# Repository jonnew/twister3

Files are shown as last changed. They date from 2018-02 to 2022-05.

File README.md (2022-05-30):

# Twister3
Twister3 is a simple and fast microwire twister from the [Wilson
Lab](http://web.mit.edu/wilsonlab/) at MIT. It is used to make tetrodes and
stereotrodes for invasive neural recordings. It can be purchased from the 
[Open Ephys store](https://open-ephys.org/twister-3).

Twister3

### Documentation
Construction, usage, and performance information is provided in the [Twister3
manuscript](https://www.biorxiv.org/content/10.1101/727644v1). Please cite 
this paper if you use Twister3 in your research. If you have further questions, 
please direct them toward the [Open Ephys forum](https://groups.google.com/forum/#!forum/open-ephys).

### Licensing
Copyright Jonathan P. Newman & Jakob Voigts 2020

<br />This work is licensed under a <a rel="license" href="http://creativecommons.org/licenses/by-nc-sa/3.0/igo/">Creative Commons Attribution-NonCommercial-ShareAlike 3.0 IGO License</a>.

If your are interested in obtaining a license to sell this device, please contact us at https://open-ephys.org/contact

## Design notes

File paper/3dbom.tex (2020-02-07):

%\externaldocument{twister3}
\setlength{\tabcolsep}{3pt}

\begin{table}[!htbp]
\centering
\caption{3D-printing bill of materials. An continuously updated bill of
    materials is located on
    \href{https://docs.google.com/spreadsheets/d/1tdc3wfE6V87q8yqBOQvDj7WylAztkh6_2kuL-YzyB0g/edit\#gid=0}{this
    Google sheet}. The right-most column provides links to order parts from each supplier.}
\label{t:3d_bom}

\begin{tabular}{llllll}
\multicolumn{4}{l}{\textit{\textbf{3D-Printing Bill of Materials}}} \\
\toprule
\textbf{Qty} &
\textbf{Description} &
\textbf{Material} &
\textbf{Supplier} &
\textbf{STL File in Repository} &
\textbf{Link} \\
\midrule

% AUTOGENERATED
1 & Feeder Base & Nylon PA12 & Shapeways & \verb|twister3_arm-base.STL| & \url{http:/shpws.me/QtfT} \\
1 & Motor Mount & Nylon PA12 & Shapeways & \verb|twister3_motor-mount.STL| & \url{http:/shpws.me/QtfL} \\
1 & Bobbin Shield & ``Fine detail plastic'' & Shapeways & \verb|twister3_bobbin-shield.STL| & \url{http:/shpws.me/QtfU}\\
2 & Bobbin Spacer & ``Fine detail plastic'' & Shapeways & \verb|twister3_bobbin-spacer.STL| & \url{http:/shpws.me/QtfR} \\
2 & Bobbin Washer & ``Fine detail plastic'' & Shapeways & \verb|twister3_bobbin-washer.STL| & \url{http:/shpws.me/QtfP} \\
4 & Bobbin & ``Fine detail plastic'' & Shapeways & \verb|twister3_bobin.STL| & \url{http:/shpws.me/QtfM} \\
1 & Rotor Base & ``Fine detail plastic'' & Shapeways & \verb|twister3_rotor-base.STL| & \url{http:/shpws.me/QtfK} \\
1 & Adjustment Plate  & ``Fine detail plastic'' & Shapeways & \verb|twister3_adjustment-plate.STL| & \url{http://shpws.me/Rekt} \\
1 & Wire Guide & ``Fine detail plastic'' & Shapeways & \verb|twister3_wire-guide-base.STL| & \url{http:/shpws.me/QtfI} \\
2 & Stock Spool Bearing Case & ``Fine detail plastic'' & Shapeways & \verb|twister3_stock-spool-bearing-case.STL| & \url{http:/shpws.me/QUtz} \\
1 & Twist Wire Aligner & Rhodium plated brass & Shapeways & \verb|twister3_twist-aligner.STL| & \url{http://shpws.me/R6mo} \\
1 & Spring Rotor Top & PEBA 2301 & Sculpteo & \verb|twister3_spring-top.STL| & \url{https://bit.ly/2H32cna} \\

\bottomrule
\end{tabular}
\end{table}

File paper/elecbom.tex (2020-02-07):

%\externaldocument{twister3}
\setlength{\tabcolsep}{3pt}

\begin{table}[!htbp]
\centering
\caption{Control box (Fig.~\ref{f:ctrl_box}) bill of materials. A continuously
    updated bill of materials is located on
    \href{https://docs.google.com/spreadsheets/d/1tdc3wfE6V87q8yqBOQvDj7WylAztkh6_2kuL-YzyB0g/edit\#gid=0}{this
    Google sheet}. Table entries labeled ``common'' are ubiquitous and
    therefore listing specific part numbers is futile due to rapid supplier
    turn over. PCB design files are located at this
    \href{https://github.com/jonnew/twister3/tree/master/control-board}{link}.
    The PCB is split into two halves separated by a breakaway v-cut. One half
    serves as the top panel of the enclosure, visible in (Fig.~\ref{f:ctrl_box}
    (B)), and the other has all electronics and is mounted beneath the front
panel.}
\label{t:elec_bom}

\begin{tabular}{lllllll}
\multicolumn{6}{l}{\textit{\textbf{Control Box Bill of Materials}}} \\
\toprule
\textbf{Qty} &
\textbf{Schematic Name} &
\textbf{Schematic Value} &
\textbf{Description} &
\textbf{Supplier} &
\textbf{Supplier Part No.} &
\textbf{Manufacturer Part No.} \\
\midrule

% AUTOGENERATED
1 & U5 & N/A & Teensy 3.2 & PRJC & & \\
& & & & & & \\
3 & M1, M2, M3 & N/A & M3 Screws, 10 mm & McMaster & 92000A120 & \\
& & & & & & \\
1 & N/A & N/A & 24V Wall Adapter & Amazon & & \\
& & & & & & \\
1 & S1 & EC12P & Rotary Encoder & Sparkfun & 10982 & EC12P \\
1 & S1 & N/A & Knob & Sparkfun & 10597 & P-15x13-T-T2-24A \\
1 & U6 & GDM1602K & LCD Display 5V & Sparkfun & 709 & GDM1602K \\
1 & N/A & N/A & Hot-Air Station & Sparkfun & 14557 & \\
& & & & & & \\
1 & For U5 & Teensy Header & 2x7 Header & Digikey & 609-3485-1-ND & 61001421121 \\
2 & For U5 & Teensy Header & 1x14 Header & Digikey & 732-5325-ND & 61301411121 \\
1 & For U5 & Teensy Socket & 2x7 Socket & Digikey & S7110-ND & PPPC072LFBN-RC \\
2 & For U5 & Teensy Socket & 1x14 Socket & Digikey & S7012-ND & PPTC141LFBN-RC \\
1 & For U6 & LCD Header & 1x16 Header & Digikey & 732-5327-ND & 61301611121 \\
1 & For U6 & LCD Socket & 1x16 Socket & Digikey & S7014-ND & PPTC161LFBN-RC \\
2 & J10, J11 & Stepper Stick Header & 1x8 Header & Digikey & 732-5321-ND & 61300811121 \\
2 & J10, J11 & Stepper Stick Socket & 1x8 Socket & Digikey & S7006-ND & PPTC081LFBN-RC \\
5 & J1, J8, J9 & N/A & 1x4 Socket & Digikey & S7002-ND & PPTC041LFBN-RC \\
3 & J3, J4, J5 & N/A & 1x4 SMD Header & Digikey & SAM12225-ND & TSM-104-02-L-SV \\
2 & For U2 & N/A & Board Spacers & Digikey & 952-3465-ND & R6010-00 \\
3 & M4, M5, M6 & N/A & M3 SMD Nuts & Digikey & 732-10918-1-ND & 9775056360R \\
1 & J2 & N/A & Screw Terminal & Digikey & ED10563-ND & OSTVN04A150 \\
1 & J1 & PJ-063BH & Barrel Jack & Digikey & CP-063BH-ND & PJ-063BH \\
4 & C2, C6, C7, C8 & 10 nF, 50 V & Capacitor, X7R & Digikey & 478-1227-1-ND & 06035C103KAT2A \\
1 & C16 & 470 nF, 10 V & Capacitor, X7R & Digikey & 1763-1190-1-ND & 0402BW474K160YT \\
2 & C1, C3 & 1 uF, 50 V & Capacitor, X7R & Digikey & 587-3247-1-ND & UMK107AB7105KA-T \\
1 & C4 & 15 uF & Tantalum Capacitor & Digikey & 399-3775-1-ND & T491D156K035AT \\
1 & C5 & 220 uF & Tantalum Capacitor & Digikey & 399-9744-1-ND & T491D227M010AT \\
1 & R6 & 470 \si{\ohm}& Resistor, Thick film & Digikey & Common & Common \\
2 & R1, R9, R10, R11, R12 & 4.7 k\si{\ohm} & Resistor, Thick film & Digikey & Common & Common \\
5 & R2, R3, R4, R5, R17 & 10 k\si{\ohm} & Resistor, Thick film & Digikey & Common & Common \\
1 & R13 & 20 k\si{\ohm} & Resistor, Thick film & Digikey & Common & Common \\
2 & R8, R16 & 20 k\si{\ohm} & Trim Pot & Digikey & SM-42TX203CT-ND & SM-42TX203 \\
1 & L1 & 68 uH & Inductor & Digikey & 513-1386-1-ND & DR125-680-R \\
1 & D1 & DB2W60400L & Schottky Diode & Digikey & P15184CT-ND & DB2W60400L \\
1 & U1 & IS31FL3193 & LED Driver & Digikey & 706-1215-1-ND & IS31FL3193-DLS2-TR \\
1 & U3 & MAX6816 & Debouncer & Digikey & MAX6816EUS+TCT-ND & MAX6816EUS+T \\
1 & U2 & MIC4680-5.0YM-TR & DC DC Converter & Digikey & 576-1221-1-ND & MIC4680-5.0YM-TR \\
1 & U4 & TMC2100 & Silent Stepper Stick & Digikey & 1460-1159-ND & N/A \\
1 & N/A & N/A & Enclosure & Digikey & 36-705-ND & 705 \\

\bottomrule
\end{tabular}
\end{table}

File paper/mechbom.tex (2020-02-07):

%\externaldocument{twister3}
\setlength{\tabcolsep}{3pt}

\begin{table}[!htbp]
\centering
\caption{Mechanical\ bill of materials. A continuously updated bill of
    materials is located on
    \href{https://docs.google.com/spreadsheets/d/1tdc3wfE6V87q8yqBOQvDj7WylAztkh6_2kuL-YzyB0g/edit\#gid=0}{this
    Google sheet}.}
\label{t:mech_bom}

\begin{tabular}{llll}
\multicolumn{4}{l}{\textit{\textbf{Mechanical Bill of Materials}}} \\
\toprule
\textbf{Qty} &
\textbf{Description} &
\textbf{Supplier} &
\textbf{Supplier Part No.} \\
\midrule

% AUTOGENERATED
1 & NEMA-17 Stepper Motor & Digikey & 1460-1163-ND \\
& & & \\
10 & 3 $\times$ 7 $\times$ 3 mm Bearings & Boca Bearing & MR73-2RSC \\
& & & \\
1 & M3 x 4mm Set screw & McMaster-Carr & 92605A098 \\
2 & M3 x 6mm Standoff & McMaster-Carr & 94868A162 \\
1 & M3 x 0.5 mm Thread Size, 500 mm Long & McMaster-Carr & 90024A219 \\
5 & M3 x 0.5 mm Thread, 40 mm Long & McMaster-Carr & 91292A024 \\
2 & M3 x 0.5 mm Thread, 60 mm Long & McMaster-Carr & 92290A131 \\
8 & M6 x 1 mm Thread, 14 mm Long & McMaster-Carr & 92855A615 \\
2 & M6 x 1 mm Thread, 25 mm Long, Set screw & McMaster-Carr & 92015A135 \\
4 & Music-Wire Steel Torsion Spring & McMaster-Carr & 9271K578 \\
2 & Zinc-Plated, M3 x 0.5 mm Thread Nut & McMaster-Carr & 90695A033 \\
2 & Dowel Pin 3/16" Diameter, 2-1/2" Long & McMaster-Carr & 98380A520 \\
& & & \\
2 & \diameter1.5" Mounting Post, M6 Taps, L = 250 mm & ThorLabs & P250/M \\
2 & Swivel-Base Mini-Post Holder, 2" (51 mm) Tall, 1/4" (M6) Slot & ThorLabs & MSL2 \\
2 & Mini-Series Optical Post, \diameter6 mm, L = 50 mm & ThorLabs & MS2R/M \\
1 & Aluminum Breadboard, 300 mm x 600 mm $\times$ 12.7 mm, M6 Taps & ThorLabs & MB3060/M \\
1 & \diameter1.5" Post Mounting Clamp, 112.5 mm $\times$ 112.5 mm, Metric & ThorLabs & C1545/M \\
& & & \\
10 & Neodymium Block Magnets, 1/8" cube & KJ Magnetics & B222G-N52 \\
2 & Neodymium Block Magnets, 1/2" $\times$ 1/4" $\times$ 1/16" & KJ Magnetics & B841-N52 \\
& & & \\
2 & Wire Clip & Digikey & 314-1017-ND \\
NA & Silicone Heat Shrink & Digikey & XX \\

\bottomrule
\end{tabular}
\end{table}

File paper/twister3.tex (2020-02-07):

\documentclass[11pt,a4paper]{article}

%\usepackage{draftwatermark}
\usepackage{booktabs}
\usepackage[T1]{fontenc}
\usepackage{graphicx}
\usepackage{hyperref}
\usepackage[margin=2cm]{geometry}
\usepackage{lineno}
\usepackage{booktabs}
\usepackage{array}
\usepackage[labelfont=bf, font=small]{caption}
\usepackage[onehalfspacing]{setspace}
\usepackage{floatrow}
\usepackage{xr}
\usepackage{siunitx}
\usepackage{enumitem}
\usepackage{wasysym}
\usepackage{siunitx}
\usepackage{placeins}
\usepackage{authblk}
\usepackage[title]{appendix}
\usepackage{array}
\usepackage{siunitx}

\DeclareFloatFont{small}{\scriptsize} % "scriptsize" is defined by floatrow
\floatsetup[table]{font=small}
\linenumbers{}
\newcolumntype{P}[1]{>{\centering\arraybackslash}p{#1}}

\title{\vspace{-2.1cm} Twister3: a simple and fast microwire twister}

\author[1,2,5]{Jonathan P. Newman \thanks{jpnewman@mit.edu}}
\author[1,3,5]{Jakob Voigts}
\author[4]{Maxim Borius}
\author[4]{Mattias Karlsson}
\author[1,3]{Mark T. Harnett}
\author[1,2,5]{Matthew A. Wilson}

\affil[1]{Department of Brain and Cognitive Sciences, MIT, Cambridge, MA, USA.}
\affil[2]{Picower Institute for Learning and Memory, MIT, Cambridge, MA, USA.}
\affil[3]{McGovern Institute for Brain Research, MIT, Cambridge, MA, USA.}
\affil[4]{SpikeGadgets LLC, San Francisco, CA, USA}
\affil[5]{Open Ephys Inc, Cambridge, MA, USA}

\begin{document}

\maketitle

\begin{abstract}
    \noindent
    We present Twister3, a microwire twisting machine. This device greatly
    increases the speed and repeatability of constructing twisted microwire
    neural probes (e.g.\ stereotrodes and tetrodes) compared to existing
    options. It is cheap, well documented, and all associated designs and
    source code are open-source. Twister3 is of interest to any lab performing
    twisted microwire neural recordings, for example, using tetrode drives.
\end{abstract}

\tableofcontents

\section{Introduction}
Since their introduction~\cite{McNaughton1983}, twisted wire probes (TWPs; e.g
stereotrodes~\cite{McNaughton1983} and tetrodes~\cite{Wilson1993, Wilson1994a})
have been a reliable method for obtaining single-unit extracellular spiking
data in freely moving animals. They are cheap ($\sim$5--10 USD/m using Sandvik
PX000004), small enough to cause minimal inflammation, and sufficiently
biocompatible to be used over many months~\cite{Dhawale2017, Voigts2013}. Their
contacts are close ($\sim$10--20 $\mu$m) and therefore allow much improved unit
separability compared to single wire probes~\cite{Gray1995}.

Compared to other commonly used electrode types, they are mechanically
flexible, such that they move with neural tissue, rather than behaving like a
rigid, skull-coupled beam. This improves long term stability compared to, e.g.,
silicon
probes\footnote{e.g.\url{http://neuronexus.com/products/neural-probes/}}, which
require second-to-second removal of artifacts due to relative shear motion
(``drift'') in order to obtain classifiable action potential
waveforms~\cite{Rossant2016,Pachitariu2016, Pachitariu2020}. In contrast, TWPs
allow units to be tracked continuously over multi-day periods with minutes-long
time-scale drift correction~\cite{Dhawale2017}, which is less deleterious to
unit classification than fast drift~\cite{Pachitariu2020}. Although the
introduction of modern silicon~\cite{Du2011,Jun2017} and carbon-fiber
probes~\cite{Gillis2018} offer major advances in terms of channel density and
size, respectively, and polyimide-substrate and mesh-electronics probes provide
orders of magnitude decreases in mechanical stiffness~\cite{Fu2017}, TWPs will
remain a ubiquitous recording method for the foreseeable future due to their
simplicity, ease of implantation, good performance, and low cost.

Although simple to make~\cite{Nguyen2009}, constructing TWPs is a tedious and
time-consuming process. For modern, easy-to-assemble microdrive
designs~\cite{Voigts2013}, making TWPs is a rate-limiting step. Typically, TWPs
are made in three actions~\cite{Nguyen2009}. First insulated tungsten or
nickel-chrome (`nichrome') resistance wire is drawn from a spool and folded by
hand 1 or 2 times to make stereo- or tetrodes, respectively. Next, the folded
wire is draped over a smooth metal rod.  The free end of the wire bundle is
loosely coupled to a motor armature using a
mechanical\footnote{\url{http://www.open-ephys.org/twister}} or
magnetic\footnote{\url{https://neuralynx.com/hardware/tetrode-spinner-2.0}}
mechanism. The motor then twists the wire bundle into a helix.  Finally, a hot
air gun is used to melt and fuse the insulation on the wire helix, forming a
springy, implantable probe.

Recently,
SpikeGadgets\footnote{\url{http://www.spikegadgets.com/main/home.html}; Note:
M.K. is co-owner and M.B. is an employee.} introduced a tetrode twisting
machine that provides an arrangement of four pre-wound wire bobbins that allows
the user to draw a multi-wire bundle without the folding
step\footnote{\url{http://www.spikegadgets.com/hardware/tetmachine.html}}.
Because folding is the most time consuming part of the TWP making process,
this device greatly improves the speed at which TWPs can be created.
Additionally, this method minimizes human wire handling, which is beneficial
because wire ends up in direct contact with neural tissue and is difficult to
clean. Despite these advantages, the high-price of its custom-designed
components ($\sim$10,000 USD) and complexity of this device has hampered its
adoption. Inspired by the SpikeGadgets design, we collaborated to create an
open-source twisting machine that is approximately ten times cheaper and ten times faster
(Fig.~\ref{f:design_features} (A)). Our device uses a high-speed stepping motor
and modern micro-stepping driver to increase twisting speed while maintaining
precise control of motor acceleration and smooth motor actuation. A new
counter-balanced, auto-aligning spring system provides constant tension on
wire during twisting. Our design allows a moderately trained ($\sim$1
hr of experience with device) operator to make $\sim$70 TWPs per hour.

\begin{figure}
\centering 
\caption{\textbf{(A)} Overview of Twister3's mechanical components. The
    motor and wire feeder assemblies are used to rapidly construct TWPs by
    drawing a wire bundle from the feeder, clipping it to the motor, and
    performing a twist. Additionally, the motor, wire guide, and stock spool
    assemblies are used to load wire onto the bobbins in the feeder after they
    are depleted.
    \textbf{(B)} Motor assembly. A NEMA-17 stepper motor is used to twist TWPs
    and reload bobbins. The wire clip, alignment jig, and magnet allow the wire
    bundle to be rapidly and reliably linked to the motor. The rotor base and
    adjustment plate allow one-time adjustment to achieve perfect alignment
    between the wire bundle and the motor axis.
    \textbf{(C)} \textit{(left)} The 3D printed leaf spring showing deformation
    under tension. The shape of the spring permits approximately vertical
    deformation of the wire attachment point so that the center axis is
    maintained as the bundle is shorted due to twisting. \textit{(right)}
    Spring tension as a function of vertical deformation. Best fit line
    indicates a spring constant of 32 nM/mm. The white dot indicates the spring deformation
    needed to oppose the wire-feeder's stiction setting for TWPs made in our lab.
    \textbf{(D)} \textit{(left)} Wire quick draw mechanism. \textit{(right)} Isolated
    single bobbin indicating the wire tension, due to the leaf spring in (C),
    and counter stiction due to the adjustable torsional spring.}
\label{f:design_features}
\end{figure}

Here we present descriptions of how this device works, materials and assembly
information, and electronics designs. We provide detailed usage
instructions, an exploration of probe mechanics with respect to twisting
parameters, TWP construction time measurements, and show data obtained with
tetrodes made using this machine. All designs and source code associated with
this project can be found on the Twister3 git
repository\footnote{\url{https://github.com/jonnew/twister3}}.

\section{Notable Design Elements}

\subsection{3D-printed Leaf Spring for Fast Twisting}
In order to achieve straight TWPs, wire must be twisted together while under
tension. In all other existing designs, a weight is hung from the wire bundle
and a motor is loosely coupled to the weight in a way that does not constrain
axial motion. This provides constant tension on the wire bundle due to gravity
while allowing the helix to decrease in length as it is twisted. A variant of
this method uses magnets hold the weight in
place\footnote{\url{https://neuralynx.com/hardware/tetrode-spinner-2.0}}, but,
in our experience, this is unnecessary and is prone to causing wire breakage
due to the nonlinear force/distance relationship of magnetic attraction.

A key design criterion for our device is that TWPs need to be turned very
quickly. We aimed for <10 seconds of twisting time (time when motor is in
motion) per TWP.\@ Assuming 100 total revolutions (upper estimate for tetrodes)
this translates to an average turn rate of 600 RPM.\@ Because previous methods
rely on loose motor coupling, they were unsuitable to meet our speed
requirements. For example, the SpikeGadgets machine, original Open Ephys
Twister, and Neuralynx Spinner-2.0 are limited to approximately 60 RPM. The
high centripetal forces involved in rapid turning inevitably leads to
instability of the coupling mechanism, causing the bundle to vibrate wildly.
Therefore, we sought to rigidly constrain the motor and wire bundle in the
turning plane, but still maintain freedom in the axial direction to allow
bundle tensioning and shortening during the turning process. To meet this goal,
we made use of selective laser-sintered polyether block amide (PEBA) to create
a monolithic, combined leaf spring/wire-retention mechanism
(Fig.~\ref{f:design_features} (B)). PEBA provides rubber-like mechanical
qualities resulting in a spring-constant low enough for use with microwire
($\sim$32 mN/mm in the relevant range of motion (Fig.~\ref{f:design_features}
(C)).

\subsection{Auto-aligning Wire/Motor Interface}
To interface the microwire bundle with the motor, the bundle is clipped
together using a standard, ferrous alligator clip that has been coated in
insulating shrink wrap. The bundle is then drawn towards the motor while the
leaf spring is lifted with with the user's free hand. While the leaf spring is
under tension, the alligator clip is attached to a strong neodymium magnet on
the leaf spring assembly, which provides the bundle-to-motor linkage
(Fig.~\ref{f:design_features} (A, B)). During this process, a 3D-printed
alignment jig on top of the magnet automatically guides the microwire bundle in
line with the motor's axis of rotation. This alignment jig must be made from a
material that can withstand the high temperature of the hot air during the
fusing process and is smooth enough to ensure it does not snag the microwire as
it guides it into position. We have found that 3D-printed rhodium-plated brass
works very well for this purpose. The leaf spring is then slowly lowered until
it reaches equilibrium with upward wire tension. At this point the motor can be
turned.

Because of print tolerances and the fact that the leaf spring does not deform
exactly vertically, the resting position of wire bundle will likely not be
perfectly co-linear with the motor axle. To account for this, the motor mount
consists of a two pieces: the base, which is rigidly concentric with the motor
shaft, and an alignment plate. The alignment plate is friction fitted within
the base and provides $\sim$2 mm of omnidirectional planar adjustment
(Fig.~\ref{f:design_features} (B)). This plate should be moved until the
resting position of the wire bundle is in line with the motor axis.

This wire attachment mechanism has two advantages over existing designs. First
it can be used rapidly because of magnetic coupling. Second, because the
microwire bundle is automatically aligned with the motor's axis of rotation,
high-turn rates do not result in oscillations or instability. We have found
that this is a critical feature in order to produce straight, even-pitch, and
consistent TWPs using very fast turn speeds.

\subsection{Quick-draw Wire Feeder}
To further increase the speed at which TWPs can be made, microwire needs to be
drawn and attached to the motor quickly. Ideally, this process should occur
with as few separate actions being taken by the operator as possible. To
facilitate the rapid draw of wire from stock spools, we designed a torsion
spring-based feeding assembly that allows wire to be quickly drawn from stock
feeder bobbins (Fig.~\ref{f:design_features} (C)).
This mechanism applies enough friction to feeder bobbins to counter increased
wire tension during a twist, transferring all slack compensation to the leaf
spring (Fig.~\ref{f:design_features} (B)). The holding (stiction) force of this
mechanism is adjustable to account for the elastic deformation of different
wire materials. We have found that, when working with standard tetrode
wire\footnote{Polyimide-coated nichrome; \diameter12.7$\mu$m}, the 2nd stiction
setting (corresponding to a threshold of $\sim$11.5 N per spool), is adequate
to counter wire tension and therefore prevent spools from improperly feeding
during a twist. However, the proper stiction setting is dependent on the
microwire material and will need to be adjusted for other wire types.

\subsection{Motor Control Hardware for Smooth Turning}
To obtain precise control over motor acceleration, speed, and position we
to used a bipolar stepper motor to perform wire twisting. We have found that,
due to their discretized motion, stepper motors can vibrate resonantly with
taut microwire, resulting in irregular twists and wire damage. To overcome
this issue, we drive our motor using an advanced microstepping driver
(Fig.~\ref{f:ctrl_box} (A));
\href{https://www.trinamic.com/products/integrated-circuits/details/tmc2100/}{Trinamic
TMC2130}). In our case, we use 200 steps/revolution (\ang{1.8})
motor. Microstep commands from the microcontroller are provided at 16
microsteps/step, which are further interpolated to 256 microsteps/step by
internal driver circuitry. This results in a motor update resolution of 3,200
microsteps/revolution (\ang{0.113}), and a motion discretization of 51,200
steps/revolution (\ang{0.007}). Therefore, the motor operates approximately as
smoothly as a continuous DC motor but with much improved motion control
dynamics.

\begin{figure}
\centering

\caption{\textbf{(A)} Control electronics block diagram. All user IO is
    provided via a combined rotary encoder and button. The Teensy's NXP
    MK20DX256VLH7 microcontroller provides a  programmable interrupt timer
    (PIT) to control step commands to the motor driver, independent of nominal
    operation.
    \textbf{(B)} Control box with callouts showing features, connections, and
    controls.}
\label{f:ctrl_box}
\end{figure}

We used an Arduino-compatible Teensy
3.2\footnote{\url{https://www.pjrc.com/teensy/teensyLC.html}} microcontroller
module to perform step timing calculation. Its NXP MK20DX256VLH7 Cortex-M4
includes an integrated programmable interrupt timer (PIT) which is used to
provide jitter-free step commands to the motor driver while acceleration
calculations are
performed\footnote{\url{https://github.com/luni64/TeensyStep}}.

\section{Usage}
The following sections provided detailed instructions for using Twister3 to
load wire and make TWPs. This content is aided by an instructional video
available on YouTube (Appendix~\ref{s:videos}).

\subsection{Using the Control Box}
The control box (Fig.~\ref{f:ctrl_box} (B)) is powered using a 12V DC
center-positive barrel jack that supplies at least 1.5A. It has a single user
input: a control knob consisting of a combined quadrature rotary encoder and
tactile push-button. This knob permits the following user actions:

\begin{itemize}[noitemsep]
    \item \textbf{Press:} cycle through different settings (forward turns,
        backward turns, turn speed, turning mode)
    \item \textbf{Turn:} increment or decrement the selected setting
        depending on turn direction.
    \item \textbf{Press and hold:} execute the turn sequence using the
        current settings
    \item \textbf{Press during motion:} cancel the twist and stop the motor
        immediately.
\end{itemize}

The control box is used to perform two tasks: twisting electrodes (mode 0)
and loading bobbins with microwire (mode 1). The turn mode is selected and
changed using the dial on the controller. The selected turn mode is shown in
the upper right corner of the liquid crystal display (LCD). After a mode is
selected, all turning parameters (speed, forward and backwards turns) pertain
to that mode only. All parameters are stored in non-volatile memory when a turn
is started by pressing and holding the control knob. In the following sections,
we detail how to use the mechanical components for making TWPs and loading
bobbins with stock wire.

\subsection{Loading Bobbins}
Before twisting electrodes, the bobbins on the wire feeder assembly must be
loaded with microwire (Fig.~\ref{f:usage}A). The following paragraphs detail
the bobbin loading procedure. A video of the bobbin loading process is
available to aid these instructions (Appendix~\ref{s:videos}).

First, the bobbins must be removed from the wire feeder assembly. To do this,
the wire shield is removed by unscrewing its M6-retention screw as indicated in
Fig.~\ref{f:feeder_assem} (6). Next, the bobbins are removed by unscrewing the
M3 bolt that serves as the bobbin axle (Fig.~\ref{f:feeder_assem} (4)). The
bobbins are then slipped off of each axle.  If the bobbins have any left-over
microwire, it should be removed and the wire grooves should be examined in to
ensure they are clean of dirt and debris. They can be wiped with a cotton swab
and water if they require cleaning.

Next, the 3D-printed leaf spring is removed from the rotor base. Because each
bobbin has embedded magnets that mate with those on the rotor base, after the
leaf-spring is removed, a bobbin can be placed onto to rotor base
(Fig.~\ref{f:usage} (A1)). Once the bobbin is in place and reasonably centered
using the adjustment plate (Fig.~\ref{f:twister3_assem}(5)), the wire guide
should be positioned such that its tip points directly into the center of the
wire groove on the bobbin.  Properly loaded bobbins will have microwire tightly
wound around their center groove. This relies on carefully adjusting the
position of the wire guide such that it's tip is located about 1--2 mm from the
center groove (Fig.~\ref{f:usage} (A1)). After this, wire is feed from from the
stock spool through the wire guide and wrapped once around the bobbin in its
center groove (Fig.~\ref{f:usage} (A2)).

Finally, to load wire onto the bobbin, the controller is set to mode 1
(Fig.~\ref{f:ctrl_box} (B)) and then the desired loading speed and number of
revolutions are selected. We have found that 100 RPM works well for most wire
(Fig.~\ref{f:ctrl_box} (B)). The circumference of the bobbin is $\sim$10 cm.
Therefore, the length of wire loaded on the bobbin is $turns \times 10\ cm$.
Including wastage, this results in a conservative estimate of 1 TWP per turn
(Table~\ref{t:tt_param}). After the desired parameters have been entered,
loading is started by pressing and holding the controller button. \textit{Be
careful not touch moving parts during this process}: the microwire needs to
have constant tension to ensure it is properly loaded on the bobbin. The
loading processes should be monitored as it begins to ensure that microwire is
being accepted by the bobbin. If there is an issue, pressing the knob on the
control unit will halt the process so it can be corrected.

Once loading has completed, the process is repeated for the for the remaining
bobbins.  After each bobbin has be loaded with microwire, they are put back on
their axle on the wire feeder assembly. Loose wire ends should point inward on
both sides of the assembly (Fig.~\ref{f:usage} (B2)). Finally, the wire shield
is replaced (Fig.~\ref{f:feeder_assem} (6)).

\begin{figure}
\centering

\captionsetup{singlelinecheck=off}
\caption[]{Bobbin loading and TWP creation procedures. 

\textbf{(A) Summary of the bobbin loading procedure. See text for details.}
\begin{enumerate}[noitemsep]
    \item The leaf spring is removed and a bobbin is magnetically mated with
        the rotor. The wire guide is moved into close proximity to the wire
        groove on the bobbin.
    \item Wire from the stock spool is threaded through the wire guide and
        around the bobbin. The control box is then used to load a desired
        amount of stock wire.
\end{enumerate}

\textbf{(B) Summary of the TWP construction procedure. See text for details.}
\begin{enumerate}[noitemsep]
    \item The leaf spring is attached to the base rotor and the wire guide is
        moved out of the way.
    \item The loose wire is alligator clipped and drawn from the bobbins. 
    \item The user's free hand is used pull up on the twisting attachment's
        leaf spring until under slight tension.
    \item The alligator clip is drawn down and flipped 180$^{\circ}$ to meet
        the magnet within the alignment jig (insets). This procedure improves
        the alligator clip's grip on the bundle. A twist can then be performed.
    \item After the twist, wires are fused \textit{starting from point at which they separate
        towards the bobbins} using a hot air gun.
    \item The bobbins are simultaneously rolled forward forward to release
        tension on the wire.
    \item The loose wire is cut e above the point at which the wires are fused,
        and the alligator clip is removed from the magnet with a finished TWP.
    \item The finished TWP is cut into a storage box.
\end{enumerate}
}
\label{f:usage}
\end{figure}

\subsection{Making Twisted Wire Probes}
The following steps detail TWP construction using Twister3. If you are
interested in making stereotrodes instead of tetrodes, follow the same steps
but only use two bobbins on diagonally opposing sides of the feeder. A video of
the TWP construction process is available to aid these instructions
(Appendix~\ref{s:videos}).

If it is not already in place, the leaf spring must be attached to the base
rotor using its magnetic interface (Fig.~\ref{f:usage} (B1)). With the leaf
spring in position, wire from each of the bobbins is grouped using a finger
pitch. The bundle is then clamped using the alligator clip (Fig.~\ref{f:usage}
(B2), Fig.~\ref{f:other_assem}(B)). The wire bundle does not need to be in a
certain position within the clip or be tightly grouped Additionally, each wire
does not need to begin at exactly the same length from the feeder because those
with more slack will not pull on their bobbin until they it is equal in length
to the shortest wire. At the point that all wires are drawing slack, they will
be equidistant from the wire feeder.

Once the wires are clamped in the alligator clip, it is flipped 180$^{\circ}$
such that the wire bundle wraps around the bottom of the clip and exits its
rear face (Fig.~\ref{f:usage} (B3, inset)). This will ensure that the wire does
not slip out of the clip as it is draw from the feeder. Do not worry if the
wire is not tightly bunched as the twist alignment jig will keep the bundle
exactly concentric with the axis of rotation during twisting. Using your free
hand, the twisting attachment's leaf spring is lifted until under slight
tension, about 1.5 cm (Fig.~\ref{f:usage} (B3)). Then, with the leaf-spring
raised, the alligator clip is drawn down to meet the magnet on the twisting
attachment, feeding the bundle into the alignment jig (Fig.~\ref{f:usage}
(B4)). After the clip is magnetically mated, the leaf spring is smoothly
lowered until it is in equilibrium with the upward force produced by the wire.
Each of the wires should be pulled straight. Do not let the spring snap back
under its tension, as this will leave slack in the wires. If any wire has
slack, its bobbin can be turned backwards slightly until it is taut. Finally,
ensure all wires are guided through the center of the alignment jig
(Fig.~\ref{f:usage} (B4, inset)) and the loose ends are not interfering with
the taught portion of the wire. If so, they should be cut before performing a
twist.

Before performing the first twist in a session, ensure that the alignment plate
has been adjusted so that the point at which the wire exits the alignment jig
is co-axial with the motor shaft (Fig.~\ref{f:twister3_assem} (5)). To do this,
adjust the position of the plate until until the point at which the wires enter
the alignment jig entry point does not "wobble" with respect to a steady
background object when the motor is manually turned back and forth. This should
only need to be done once per session. After alignment, the controller is set
to mode 0 and the desired number of turns and turn speed are selected
(Fig.~\ref{f:ctrl_box}(B)). We use 900 RRM for our wire
(Table~\ref{t:tt_param}). These settings only need to be entered once because
they are saved to non-volatile memory by the controller every time they are
changed. The button is then pressed and held to start a twist.

After the twist is complete, the wires are fused using hot air. The exact
parameters of the hot air gun will dependent on the melting point of microwire
insulation material. For polyimide, we have found that 480
$\sim$\SI{480}{\celsius} is a good temperature. We have found that the air flow
is not critical, but should not be so high that it deforms the taught wire
during the fusing process. Settings for our hot air gun
(Table~\ref{t:elec_bom}) lab are provided in Table~\ref{t:tt_param}.

Once the air gun has reached a stable temperature, the nozzle is held $\sim$5
mm from the from the point at which the twisted microwires separate towards the
feeder bobbins (Fig.~\ref{f:usage} (B5)). It is then moved downward slowly and
smoothly ($\sim$2 cm/s) until it reaches the wire alignment jig. The direction
is then reversed and it is raised until the nozzle returns to its initial
position at the wire separation point. The nozzle is then moved away from the
wire. Starting from the top and fusing downward is important: we have found
that fusing from the bottom and moving upwards will cause the lower portion of
the TWP to `absorb' slack from above resulting in a very fine twist pitch and a
TWP that is shorter than intended.

After wire fusing, both hands are used to simultaneously roll each of the
bobbins forward until the leaf spring relaxes and there is no tension on the
microwire (Fig.~\ref{f:usage} (B6)). The loose wire above the fused TWP is
then cut using scissors (Fig.~\ref{f:usage} (B7)). When performing this cut,
make sure to leave enough free wire for connectorization. Finally, the
alligator clip is removed from the magnet in the wire alignment jig and  the
finished TWP is cut into a storage box (Fig.~\ref{f:usage} (B8)). The process
can then be repeated for the next TWP.

\subsection{Selecting Device Parameters}
Choosing twisting parameters will require some experimentation in order to
produce TWPs with the desired geometric and mechanical properties given the
user's choice of wire, implant type, and animal model. In our labs, we use
Twister3 to make tetrodes for microdrive implants in both mice and rats. The
operation settings that we use are shown in Table~\ref{t:tt_param}. 

Two settings of note are the height of the wire feeder above the motor
assembly, which determines the probe length and microwire twist pitch and the
bobbin stiction threshold which determines the wire tension during twisting and
drawing. Figure~\ref{f:trode_char} shows the effect of changing the wire
feeder height on resulting tetrode characteristics for 12.7 $\mu$m diameter,
polyimide coated nichrome and 0.6 $\mu$m, polyimide coated nichrome mircowire
types. For both wire types, lowering the feeder closer to the motor, and
therefore increasing the angle of wire divergence from the axis of rotation
does decrease twist pitch and probe length for a given number of turns.
However, the buckling point (Fig.~\ref{f:trode_char}) and stiffness
(Fig.~\ref{f:trode_char}) of tetrodes across feeder heights for each material
are remarkably stable. Probe stiffness across materials and wire diameters is
very different, as expected.

To test probe functionality, we produced tetrodes using the device settings in
Table~\ref{t:tt_param}. Using procedures that were approved by the
Committee on Animal Care of Massachusetts Institute of Technology and followed
the ethical guidelines of the US National Institutes of Health, these tetrodes
were gold plated~\cite{Nguyen2009} and used in combination with microdrive
assemblies~\cite{Voigts2013,Kloosterman2009} to obtain recordings in the
pyramidal cell layer of CA1 of mice and rats. As expected, these tetrodes
reliably produced characteristic LFP and multiple, well-isolated units in both
mice (Fig.~\ref{f:trode_char}(D)) and rats (Fig.~\ref{f:trode_char}(E)).

\begin{table}[!htbp]

\centering
\caption{Materials, operation parameters, and resulting tetrode features as
    Twister3 is used in our labs. Critical settings are the feeder height,
    which controls the TWP pitch and bobbin torsion, which controls wire
    tension. \small\textsuperscript{*}Using the hot air station specified in
    the bill of materials, this is the lowest setting used in combination with
    8 mm diameter nozzle \small\textsuperscript{$\dagger$}Mean $\pm$ standard
    deviation over three novice users (Fig.~\ref{f:tt_time})
}
\label{t:tt_param}

\begin{tabular}{rlP{3cm}P{3cm}}
\toprule
                    &                                           & \textbf{Mouse}   & \textbf{Rat}      \\
\cmidrule{3-4}
\textbf{Materials}  & Microwire                                 & \multicolumn{2}{c}{Sandvik PX000004} \\
                    &                                           & \\
\textbf{Hardware}   & Feeder height                             & \multicolumn{2}{c}{49 cm from base to bobbin axle} \\
\textbf{Settings}   & Bobbin stiction                           & \multicolumn{2}{c}{Set point 2 ($\sim$11.5 mN)} \\
                    & Hot air temp                              & \multicolumn{2}{c}{\SI{480}{\celsius}} \\
                    & Hot air flow\textsuperscript{*}           & \multicolumn{2}{c}{$\sim$5.8 L/m} \\
                    &                                           & \\
\textbf{Turn}       & Forward turns                             & 40               & 60 \\
\textbf{Settings}   & Reverse turns                             & 10               & 15 \\
                    & Turn speed                                & \multicolumn{2}{c}{900 RPM} \\
                    &                                           & \\
\textbf{Results}    & TWP length                                & 37 mm            & 55 mm \\
                    & Twist pitch                               & \multicolumn{2}{c}{1.18 mm} \\
                    & Avg.\ load time\textsuperscript{$\dagger$} & \multicolumn{2}{c}{21.1 $\pm$ 10.0 sec} \\
                    & Turn time                                 & 8 sec           & 9.5 sec \\
                    & Avg.\ fuse time\textsuperscript{$\dagger$} & \multicolumn{2}{c}{11.1 $\pm$ 5.6 sec} \\
                    & Avg.\ cut/removal time\textsuperscript{$\dagger$}  & \multicolumn{2}{c}{11.3 $\pm$ 4.5 sec} \\
                    & Avg.\ TWP time\textsuperscript{$\dagger$}  & 51.5 $\pm$ 9.6 sec &  53.0 $\pm$ 9.6 sec \\

\bottomrule
\end{tabular}
\end{table}

\begin{figure}
\centering

\caption{Tetrode characteristics for different twist pitches and wire types.
    \textbf{(A)} \textit{(right)} Diagram of the mechanical test. Tetrodes were
    attached to a rigid column and the exposed portion cut to a length $L$. The
    rigid column was lowered in small increments using a micro-manipulator onto
    a precision scale and the resulting force was measured to find the buckling
    point. \textit{(middle)} Feeder height versus twist pitch, probe length,
    diameter, and average stiffness across exposed lengths when using nichrome
    or tungsten microwire of different diameters. Aside from the feeder height,
    all other construction parameters were kept the same as the rat column of
    Table~\ref{t:tt_param}. The circled row indicates the parameters used to
    create the tetrodes that produced the data in panels (D) and (E).
    \textit{(right)} Micrographs of sections of probe shanks for each twist
    pitch and material presented in the table. Each arrow-line is a quarter
    pitch.
    \textbf{(B)} \textit{(left)} Compressive force versus depth lowered
    ($\delta L$) onto a rigid surface. Each line is a single tetrode sample cut
    to one of 5 exposed lengths ($L$ = 25, 20, 15, 10, and 5 mm). Data point
    symbols correspond to the nichrome portion of table in (A) for various
    probe lengths. The buckling force (value at which there is no increase in
    restorative force with $\delta L$) is length dependent. Different exposed
    probe lengths form clear groupings with the bucking force increasing as the
    probe length gets shorter. \textit{(right)} Buckling forces for each sample
    on a log scale.  The buckling force is clearly grouped for each probe
    length but is not affected by twist pitch.
    \textbf{(C)} Stiffness versus probe length for each of the nichrome samples
    tested in (A). Of the parameters tested, longer, wide-pitch TWPs tended to
    be stiffest.
    \textbf{(D)} Example hippocampal mouse CA1 recording during sleep.
    \textit{(top)} Raw voltage trace from a single tetrode. Three sharp
    wave-ripple events are clearly visible in the trace. \textit{(bottom)}
    Spike amplitudes for each combination of two wires on the tetrode.
    \textbf{(E)} Example hippocampal rat CA1 recording during sleep.
    \textit{(top)} Raw voltage trace from a single electrode. Multiple sharp
    wave-ripple events are clearly visible in the trace. \textit{(bottom)}
    Spike amplitudes for each combination of two wires on the tetrode.
    Recordings in (D) and (E) are skull referenced.
}

\label{f:trode_char}
\end{figure}

\subsection{TWP Construction Time}
To quantify Twister3's speed of operation, we measured the tetrode construction
time of three users. All users had $\sim$1 hour of experience with the device
at the time of testing (Fig.~\ref{f:tt_time}). We divided speed measurements
into three steps: \textit{(1)} wire clipping/drawing, \textit{(2)} wire
twisting/fusing, and \textit{(3)} tetrode removal and storage.  Time trials
were performed using the device parameters shown the ``Mouse'' column of
Table~\ref{t:tt_param}. The motor-in-motion time was constant (9.1 sec at
1000 RPM max speed) and therefore incurred a constant offset on step (2), as
indicated by the dashed line in Figure~\ref{f:tt_time}. All users were able to
create tetrodes at a pace exceeding 1 tetrode/minute. However, each user had
slightly different strategies when using the device. For instance, user 3, who
has large amounts of experience with tasks requiring fine motor skills, was
relatively quick for steps (1) and (3) and was relatively slow for the fusing
step (2).  User 1 had occasional difficulty clipping and the wire during step
(1), increase their average time. These discrepancies indicate that there is
room for future improvement and automation, especially with respect to wire
clipping and fusing.

\begin{figure}
\centering

\caption{
    Tetrode construction time of users with $\sim$1 hour of experience with
    Twister3. \textit{(left)} Total construction time for each tetrode
    (symbols), average time across tetrodes for each user (thin lines), and across all tetrodes and users (thick
    line). \textit{(right)} Timing for each step of tetrode construction.
    The dotted line above the turn and fuse step is the constant motor-in-motion
    time. Twister3 parameters were the same as the ``Mouse'' column of
    Table~\ref{t:tt_param}.
}
\label{f:tt_time}
\end{figure}

\section{Materials and Assembly}
A potentially updated bill of materials (BOM) for electrical, mechanical and
3D-printed parts is available on a Google
sheet\footnote{\url{https://bit.ly/2H2a4FD}}. Instructions for component assembly are
provided in the following sections. For ease of reference and permanence, we
provide snapshots of current BOMs in Appendix~\ref{s:boms}. However, the online
versions should be used during Twister3 assembly to ensure up to date suppliers
and error corrections.

\subsection{Mechanical Components}
The mechanical portion of Twister3 consists of common hardware, standard
optomechanical components, and 3D-printed parts. Wherever possible, we used
standard (and easy to replace) parts. The mechanical bill of materials is shown
in Table~\ref{t:mech_bom}. In addition to these standard mechanical components,
several 3D-printed parts are required (Table~\ref{t:3d_bom}). These parts are
available for direct purchase from third-party 3D-printing services via the
links provide in the table. After obtaining the required components, the wire
feeder, wire-guide, and stock-spool assemblies can be constructed by following
steps detailed Figures~\ref{f:feeder_assem},~\ref{f:other_assem}
(A),~\ref{f:other_assem} (B), and~\ref{f:other_assem} (C), respectively. After
each of these modules is complete, they are combined into the complete device
by following the steps presented in Figure~\ref{f:twister3_assem}.

\begin{figure}
\centering
\captionsetup{singlelinecheck=off}

\caption[]{Wire feeder assembly.
\begin{enumerate}[noitemsep]
    \item Insert press-in components into the feeder base. This includes M3 nut
        (2x), M3 standoff (2x), and 3/16'' diameter dowel pin (2x). This
        requires a mallet.
    \item Mount the feeder base unto the C1545/M mounting clamp using M6 screws
        (2x). The top of the feeder should be flush with the mounting clamp.
    \item Cut two 5 cm sections from the M3 threaded rod. Turn each section
        into the M3 nut which behind the feeder base. The position of the rod
        determines the stiction on each bobbin during wire draw. Lower
        positions provide less stiction. We have found that the second notch is a
        good position to start with.
    \item Use the 60 mm M3 screw to mount the bobbin assembly to the standoff
        captive within the feeder base. Repeat for both sides. The thumb-screw
        head should be glued onto the M3 screw using epoxy prior to this step.
    \item Thread a torsional spring onto the dowel pin. Squeeze it together
        and then set it between the threaded rod on one side and the shallow
        groove in each bobbin on the other. Repeat for each bobbin.
    \item Install the wire shield above the bobbins using a single M6 screw.
\end{enumerate}}
\label{f:feeder_assem}
\end{figure}

\begin{figure}
\centering
\captionsetup{singlelinecheck=off}

\caption[]{Other mechanical assemblies.

\textbf{(A) Motor assembly.}
\begin{enumerate}[noitemsep]
    \item Remove the long, M3 step screws from the bottom of the stepper motor
        (4x).
    \item Use 40 mm M3 screws (4x) to attach the motor mount to the bottom of
        the motor.
    \item Fix the rotor base onto the shaft with the M3 set screw.
    \item Press fit two magnets into the alignment plate \textit{in the same
        orientation}. Make sure they are pushed down until recessed below the
        plastic surface so that they do not interfere with the flat mating
        surface of the piece.
    \item Insert the alignment plate into the slot on the rotor base.
    \item Attach two \textit{additional} magnets on top of those you just
        inserted into alignment plate. Press the spring rotor onto these
        magnets to press fit them into the spring rotor base. This procedure
        ensures that magnets will be press fit into the spring rotor base with
        the correct polarity.  Make sure the magnets are recessed below the
        bottom surface of the spring rotor so that it rests flat on top of the
        alignment plate.
    \item Push the clip magnet into one of the slots on the spring rotor top.
        In the remaining slot, press the twist alignment jig into position over
        the magnet.
\end{enumerate}

\textbf{(B) Wire clip assembly.}
\begin{enumerate}[noitemsep]
    \item Put two pieces of heat shrink tubing over the wire clip jaws.
    \item Shrink into position using the hot air gun. This prevents electrode
    wire from slipping during a draw. The clip can then be stuck under the
    wire alignment jig (Fig.~\ref{f:usage}).
\end{enumerate}

\textbf{(C) Wire guide assembly.}
\begin{enumerate}[noitemsep]
    \item Screw the wire-guide into a mini, 6 mm diameter optical post.
    \item Push the optical post into a swivel post holder.
\end{enumerate}

\textbf{(D) Stock spool assembly.}
\begin{enumerate}[noitemsep]
    \item Push a bearing into each of the stock spool bearing cases.
    \item Push each of the bearing cases into the stock spool of microwire.
    \item Push a 40 mm, M3 screw through the two bearings and screw into a mini,
        6 mm diameter optical post.
    \item Push the optical post into a swivel post holder.
\end{enumerate}
}

\label{f:other_assem}
\end{figure}
\FloatBarrier

\begin{figure}
\centering
\captionsetup{singlelinecheck=off}

\caption[]{Twister3 assembly.
\begin{enumerate}[noitemsep]
    \item Screw together the large, 1.5" diameter mounting posts and then screw
        this long post into either the left or right side of the optical bread
        board. Mount the stock spool assembly in on the opposite side of the
        optical breadboard using a M6 screw. Its exact position does not matter.
    \item Mount the feeder assembly on the post using the post mounting clamp
        on its back.
    \item Mount the rotor assembly directly in front of the post, as close as
        it will go, using 3 M6 screws.
    \item Mount the wire guide assembly into a position that is in close
        proximity to the motor assembly using a single M6 screw. The tip of the
        wire guide should be able to extend into the center grove of a wire bobbin
        when it is mounted on the rotor bases for wire reloading.
    \item With the wire-clip mechanism installed, slide the adjustment plate
        around until the motor axis of rotation (dotted black line) is precisely
        in line with the wire bundle (red lines). When properly aligned, the apex of
        the wire bundle will appear motionless during motor turning.
\end{enumerate}
}
\label{f:twister3_assem}
\end{figure}

\FloatBarrier

\subsection{Control Electronics}
The control board is comprised of the following blocks: power regulation,
motor-driver, microcontroller, and user interface (Fig.~\ref{f:ctrl_box} (A)).
Wherever possible, we used pre-assembled modules (microcontroller, motor
driver, and LCD display). The bill of materials for this board is shown in
Table~\ref{t:elec_bom}. Printed circuit board designs and Gerber files are
available on the Twister3
repository\footnote{\url{https://github.com/jonnew/twister3/tree/master/control-board}}.

\section{Discussion}
There are several device options for making TWPs. These broadly fall into two
categories: \textit{(1)} Twisters with a manual wire folding step, and
\textit{(2)} Pre-loaded bobbin designs. Devices such as the Open Ephys
Twister\footnote{\url{http://www.open-ephys.org/twister}}, Matt Gaidica's
Simple Twister\footnote{\url{http://www.open-ephys.org/simple-twister}}, and
the Neuralynx
Spinner-2.0\footnote{\url{https://neuralynx.com/hardware/tetrode-spinner-2.0}}
fall into the first category. The first of these two devices are very cheap and
simple, and may be ideal for labs who do not need to make many TWPs and can
accept some TWP construction variability. However, a general disadvantage with manual
folding machines is that they are slow. This is due to a  manual folding step
combined with loose mechanical coupling that requires slow turning speeds.  A
single TWP generally takes several minutes to make, even for an experienced
operator. This can be partially mitigated by using these devices in
parallel: a second TWP is folded while the first is turned. However, we have
found that due to the finicky nature of the folding step, using any more than
two devices at a time is nearly impossible. Further it places a large rote
labor burden on the operator, which can lead to poor construction quality due
to boredom.

Aside from slow construction speed, these devices introduce large (and
uncontrollable) variability in manual wire handling and twist-pitch (which is
directly linked to electrode compliance (Fig.~\ref{f:trode_char})). Although
they are cheaper than bobbin-based designs, their manual labor requirements and
slow operation lead to human-resource requirements that can far outweigh the
increased material cost of bobbin-based designs.

There are two options for pre-loaded bobbin TWP machines: Twister3 and the
SpikeGadgets Tetrode
Machine\footnote{\url{http://www.spikegadgets.com/hardware/tetmachine.html}}.
Although similar in principle of operation, these two designs use different
strategies at nearly every component resulting in very different user
experiences and cost. We have summarized these differences in
Table~\ref{t:compare}.

\setlength{\tabcolsep}{10pt}

\begin{table}[!htbp]
\centering
\caption{Comparison of Twister3 and SpikeGadgets Tetrode Machine.}
\label{t:compare}

\begin{tabular}{rll}
\toprule
&
\textbf{SpikeGadgets} &
\textbf{Twister3} \\
&
\textbf{Tetrode Machine} &
\textbf{(this device)} \\

\cmidrule{2-3}

\textbf{Wire feed mechanism}            & Spring-loaded clamp   & Torsion-spring quick draw  \\
\textbf{Automatic wire fusing}          & Yes                   & No \\
\textbf{Wire/motor-axis alignment}      & No                    & Yes \\
\textbf{TWP turning motor type}         & Continuous DC         & Stepper \\
\textbf{Wire fuser motor type}          & Stepper               & N/A \\
\textbf{Motor controller}               & Standard half-bridge  & TMC2130 \\
\textbf{TWP turning speed}              & 60 RPM typical        & 700--1000 RPM typical \\
\textbf{Acceleration control}           & No                    & Yes \\
\textbf{Bobbin/motor attachment}        & Screw                 & Magnets \\
\textbf{Wire bundle/motor attachment}   & Free-hanging          & Leaf-spring \& magnet \\
\textbf{Microcontroller module}         & Arduino Due           & Teensy LC \\
\textbf{Adjustable twist geometry }     & No                    & Yes \\
\textbf{Mechanical parts}               & Custom machined       & Standard optomechanics \& 3D printed \\
\bottomrule
\end{tabular}
\end{table}

The two most notable differences between Twister3 and the SpikeGadgets Tetrode
Machine are the means by which they increase TWP construction speed and the
wire fusing mechanism. Twister3 provides automatic wire bundle alignment and a
leaf-spring based bundle to motor coupling, instead of relying on gravity to
provide wire tension. This means that wire can be turned at fast
speeds while maintaining twist integrity. Because wire turning only takes a few
seconds, it is not a rate limiting step in the TWP construction process.
Because the SpikeGadgets device lacks Twister3's motor coupling features, it
must turn TWPs relatively slowly ($\sim$60 RPM vs. $\sim$1000 RPM).

To compensate for its slow turn rate, the SpikeGadgets machine permits
efficient construction via parallelization. Wire is turned slowly, but a linear
actuator and hot air gun are used to perform the fusing step automatically. The
benefit of this strategy is twofold: (1) increased repeatability of the fusing
step, and (2) manual labor is only required for clipping the wire bundle
to the motor. This allows 3 identical twisting units to be used in parallel,
increasing the effective TWP construction rate to the point where there is
effectively no user downtime. The downside of this strategy is a major increase
in materials cost and design complexity compared to Twister3. However, given
the additional benefits of automated wire fusing, we see this feature as
obvious target for future improvement of Twister3.

Aside from these two primary differences, Twister3 also affords several other
improvements compared to the SpikeGadgets device. Twister3 provides precise
acceleration control, quick-draw wire feeding, rapid magnetic wire bundle to
motor attachment mechanism, and automatic wire tensioning. These features
simplify operator use in comparison to the SpikeGadgets machine. Further, our
use of standard optomechanical and cheap 3D printed parts greatly reduces BOM
cost and increases ease of acquisition compared to SpikeGadgets design, which
relies on custom, tight-tolerance machined parts.

A construction step that is not currently addressed by any TWP machine is the
precision cut used to create the exposed probe tip. The most common "final cut"
method is to place the TWP in a single groove between the serrations of
well-maintained, hard (tungsten or carbide-coated) scissors and then
manually close them~\cite{Nguyen2009,Ferguson2009a}. This typically creates
TWPs without electrical shorts, but does not result in consistent
cross-sectional electrode geometry when the tips are viewed using electron
microscopy~\cite{Ferguson2009a}. More consistent geometry can be obtained by
performing this cut with the shaft submerged in liquid nitrogen which makes the
insulating material brittle. However, both of these procedures are tedious and
variable and therefore lend themselves to automation. Automated TWP
shearing could perhaps be incorporated into the Twister3 design in the future.

Because TWPs provide a good balance of data quality, ease of use, ease of
assembly, and low cost, they will continue to be used in \textit{in vivo}
neurophysiology labs for years to come. Twister3 is a simple device that
greatly decreases manual labor, greatly increases TWP production speed and
quality, and is affordable for most labs that might benefit from it. It is
fully open-source, well-documented (via this manuscript and instructional
videos (Appendix~\ref{s:videos})), and is composed of easy to obtain parts.
Further, we encourage the replication and improvement of this device by others.
For instance, an open design that incorporates the automated wire fusing step
would further reduce human variability in TWP quality of the current design. We
hope that Twister3 complements the growing number of open-source
electrophysioloy tools, such as
microdrives~\cite{Kloosterman2009,Voigts2013}, electrical
stimulators~\cite{Cermak2019}, optical
stimulators~\cite{Newman2015}\footnote{\url{https://github.com/jonnew/cyclops}},
acquisition hardware~\cite{Siegle2017}, electrode impedance
testers~\cite{Matsumoto2019}, and software~\cite{Newman2012b, Siegle2017,
Lopes2015}. Combined with a growing ecosystem of open-source hardware, e.g.\
for microscopic imaging~\cite{Cai2016,Voigt2019,MIMMS}, DNA
amplification~\cite{OpenPCR}, audio monitoring~\cite{Hill2018}, culture
plate-reading~\cite{Szymula2019}, bacterial evolution~\cite{Takahashi2015}, and
closed-loop small animal experimentation~\cite{Maia2017,Moreira2019}, these
tools will permit labs to be completely outfitted with high-performance,
low-cost, open-source tools. We believe this trend will increase the
accessibility, transparency, and quality of scientific research in
general~\cite{Siegle2015}.

\section*{Acknowledgments}
The authors gratefully acknowledge Ming-fai Fong for her detailed review of the
manuscript. Additionally, we thank Marie-Sophie Helene van der Goes and Dimitra
Vardalaki for their helpful feedback on the device design as well as
participating in time trial testing. Finally, we thank Hector Penagos for
providing the tetrode recordings from mice and rats presented in
Fig.~\ref{f:trode_char} of this manuscript.

This work was supported by the Center for Brains, Minds and Machines (CBMM),
MIT, funded by NSF STC award CCF-1231216. JPN was supported by the NIH (NRSA
1F32MH107086-01). JV and MTH were supported by funding provided by the NEC
Corporation Fund for Research in Computers and Communications at MIT and the
NIH (1R01NS106031). JV is a Simons Center for the Social Brain at MIT
postdoctoral fellow and MTH is a Klingenstein-Simons Fellow in Neuroscience, a
Vallee Foundation Scholar, and a McKnight Scholar.

\section*{Conflicts of Interest Statement}
JV, JPN and MW are board members of Open Ephys inc., a nonprofit that supports
the development, standardization, and distribution of open-source tools for
neuroscience research. The work described in this manuscript is being
distributed through Open Ephys. None of the authors are receiving any financial
compensation for their position on the board or for the work described in this
manuscript.

\medskip

\bibliographystyle{unsrt}
\bibliography{twister3}

\newpage

\begin{appendices}

\section{Instructional Videos}\label{s:videos}

Videos documenting device operation and usage are available on YouTube:

\begin{itemize}
    \item \textbf{\url{https://youtu.be/xQbXc738ZuM}} Annotated video showing
        how to use Twister3 to load bobbins with electrode wire and how to use
        Twister3 to make tetrodes.
    \item \textbf{\url{https://youtu.be/B0MdM4z-wl0}} Video showing the
        construction of two tetrodes, start to finish.
\end{itemize}

\section{Bills of Materials}\label{s:boms}

\input{mechbom}
\input{3dbom}
\input{elecbom}

\end{appendices}

\end{document}

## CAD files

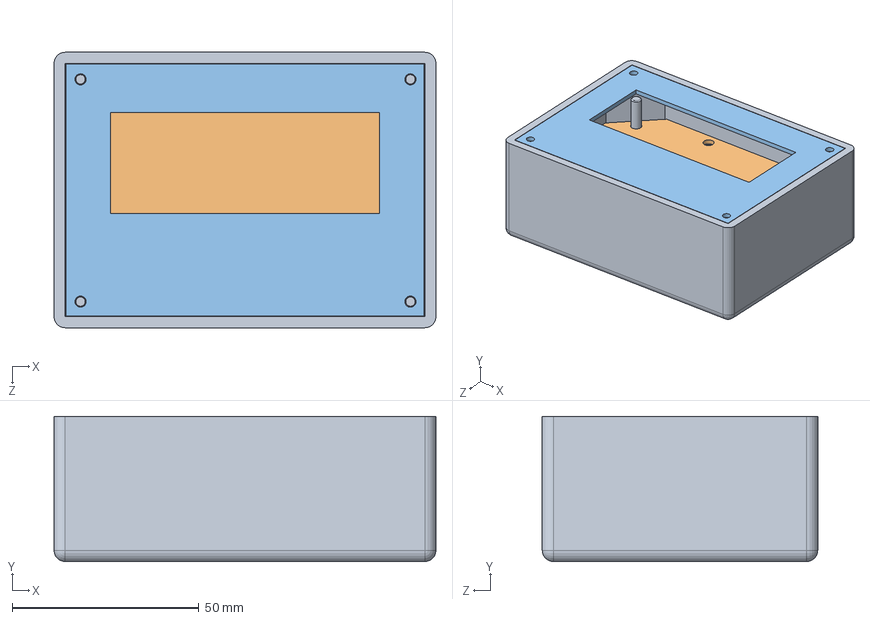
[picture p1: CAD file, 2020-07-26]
control-board/box/controller-box-assem.SLDASM
102.3 x 38.9 x 73.8 mm
controller-box
bottom-pcb
top-pcb

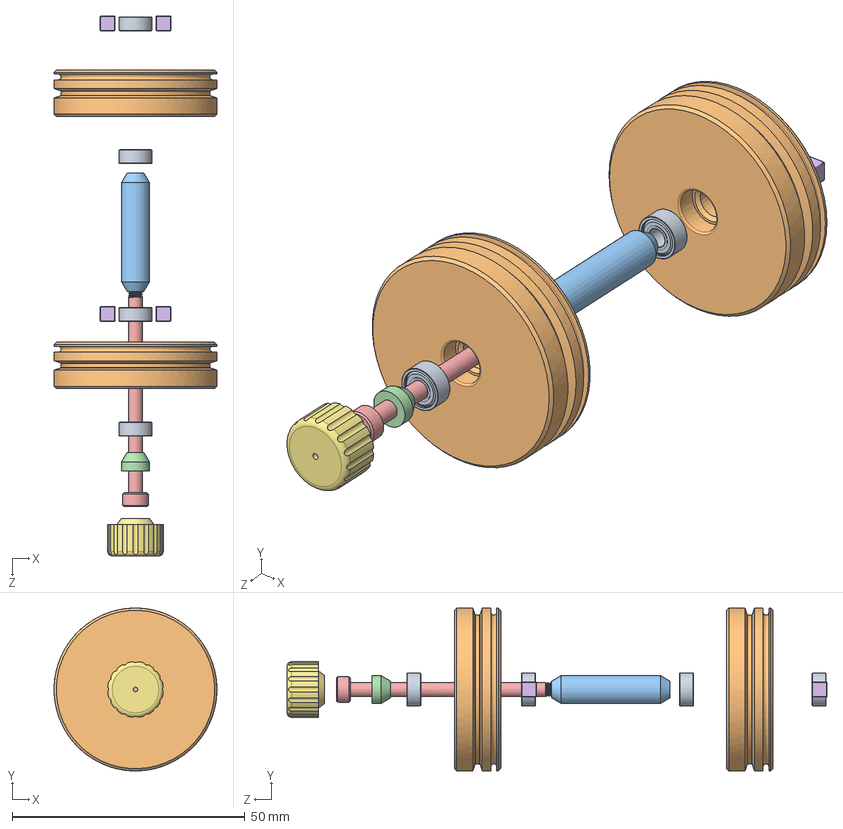
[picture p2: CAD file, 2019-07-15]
cad/twister3_bobin.SLDASM
35.0 x 35.0 x 116.0 mm
SMR73C_YZZ_AF2-bearings x 4
twister3_bobin x 2
twister3_bobbin-spacer
twister3_bobbin-washer
92290A131_TYPE 316 SS SOCKET HEAD CAP SCREW
B222G-N52_kj-magnets x 4
twister3_screw_thumbwheel

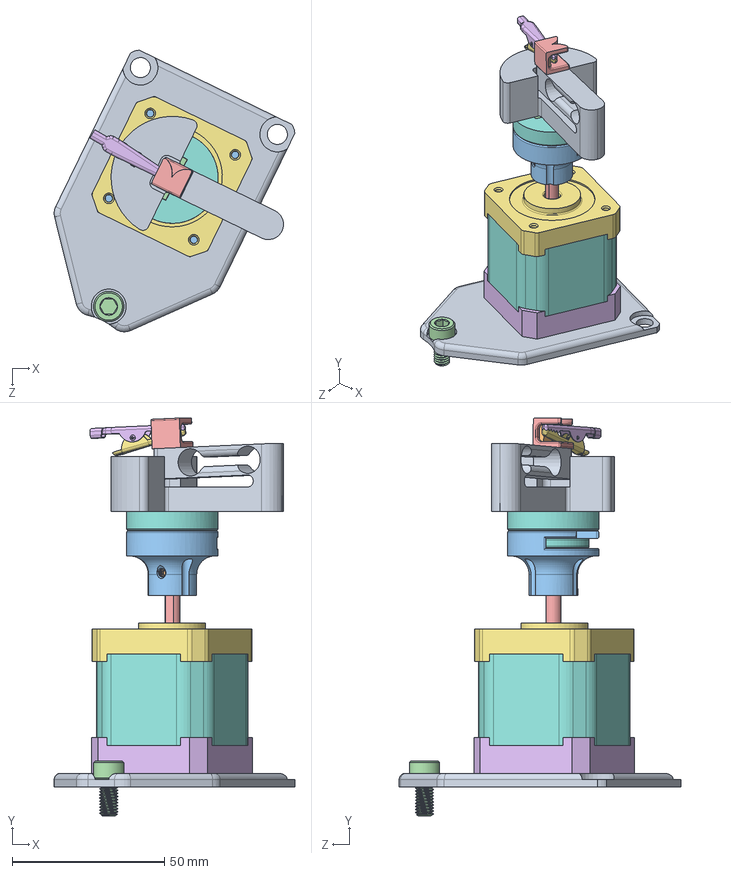
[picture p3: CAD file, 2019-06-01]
cad/twister3_trode-spinner.SLDASM
79.0 x 130.6 x 92.4 mm
twister3_spring-top
B841-N52_kj-magnets
twister3_spring_rotor_base
B222G-N52_kj-magnets x 4
NEMA 17 Stepper Motor Shaft
NEMA 17 Stepper Motor Bottom
NEMA 17 Stepper Motor Top
NEMA 17 Stepper Motor Middle
twister3_motor-mount
93245A098_NONMARRING FLAT POINT SOCKET SET SCREW
92005A136_METRIC PAN HEAD PHILLIPS MACHINE SCREW x 4
twister3_twist-aligner_independent
twister3_spring_rotor_mount

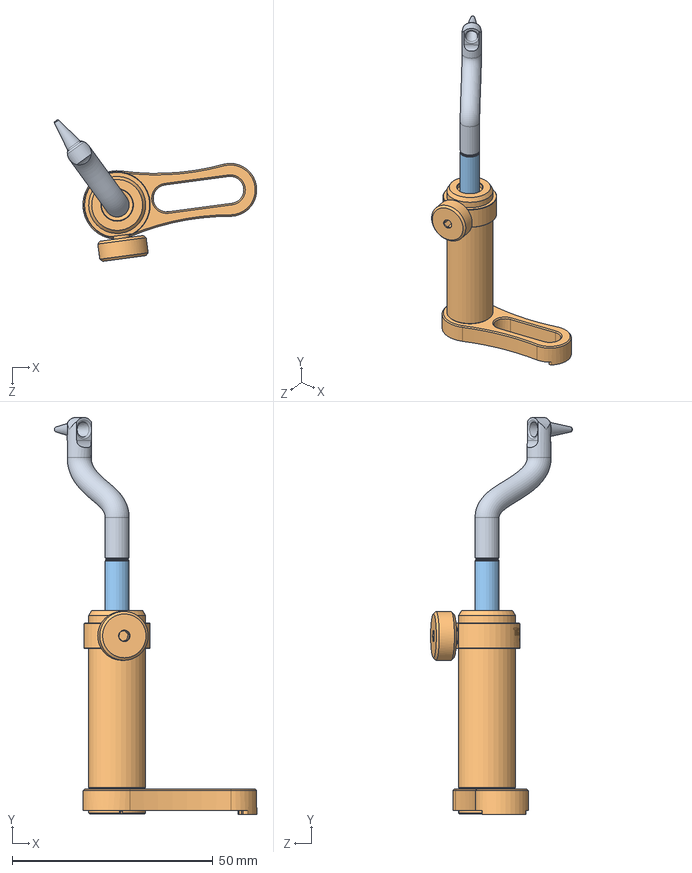
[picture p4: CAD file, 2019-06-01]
cad/twister3_wire-guide.SLDASM
50.5 x 99.0 x 35.4 mm
twister3_wire-guide-base
MSL2-Solidworks
MS2R_M-Solidworks

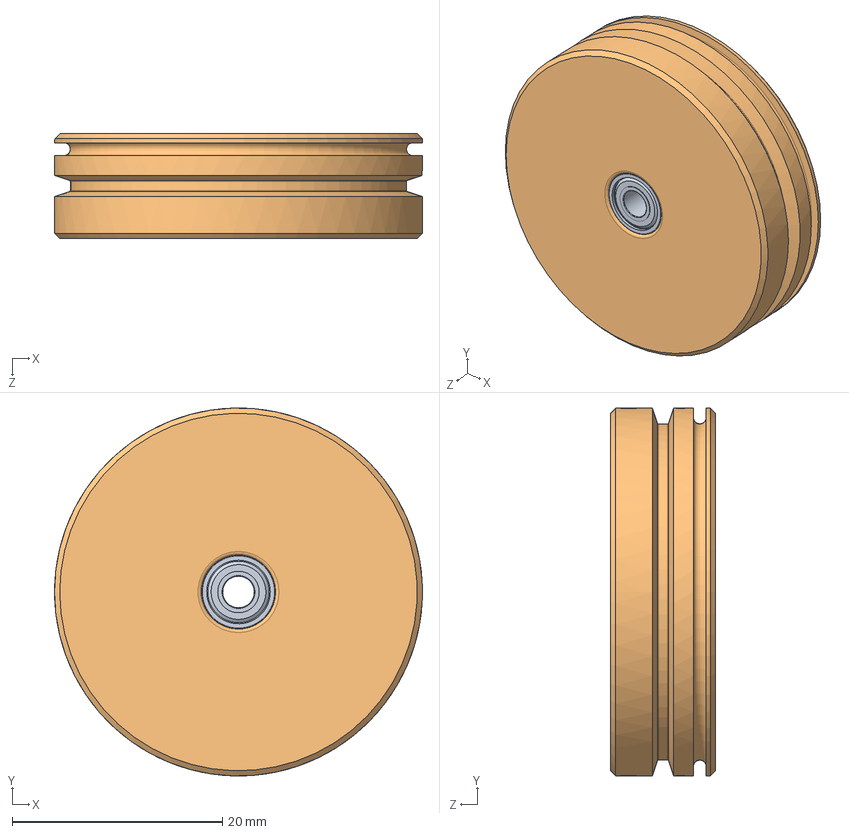
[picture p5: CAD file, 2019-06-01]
cad/twister3_single-bobin.SLDASM
35.0 x 35.0 x 10.0 mm
SMR73C_YZZ_AF2-bearings x 2
twister3_bobin
B222G-N52_kj-magnets x 2

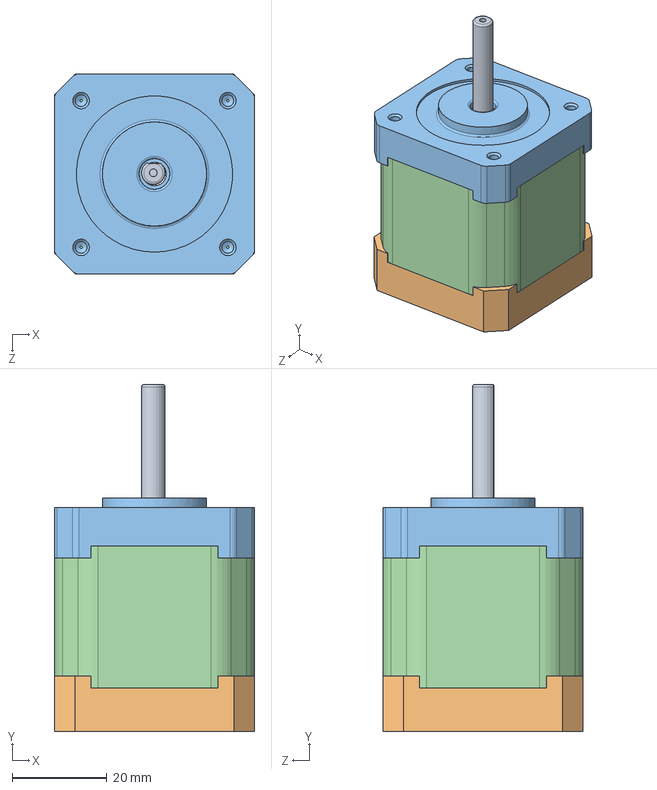
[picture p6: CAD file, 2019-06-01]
cad/NEMA 17 Stepper Motor Assembly.sldasm
42.3 x 73.3 x 42.3 mm
NEMA 17 Stepper Motor Shaft
NEMA 17 Stepper Motor Bottom
NEMA 17 Stepper Motor Top
NEMA 17 Stepper Motor Middle

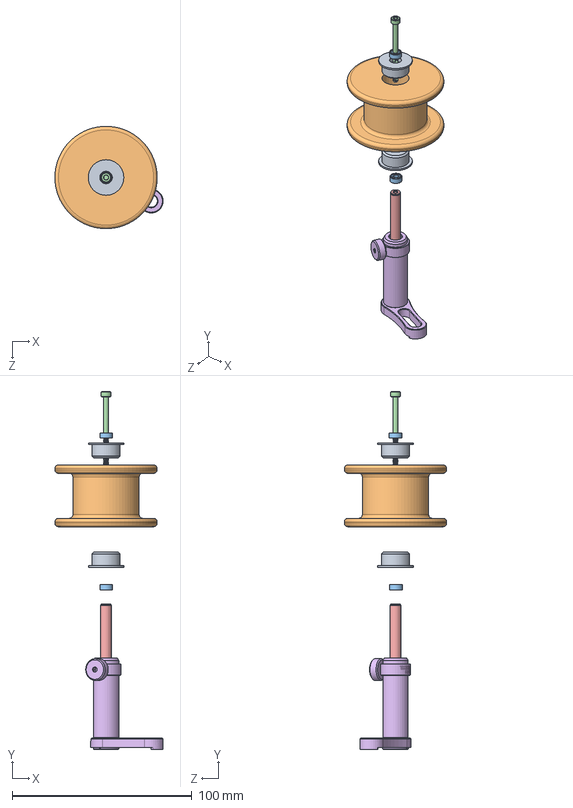
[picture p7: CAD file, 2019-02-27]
cad/twister3_stock-spool.SLDASM
60.3 x 199.4 x 57.0 mm
twister3_stock-spool-bearing-case x 2
twister3_stock-spool
SMR73C_YZZ_AF2-bearings x 2
91292A024_TYPE 18-8 SS SOCKET HEAD CAP SCREW
MS2R_M-Solidworks
MSL2-Solidworks

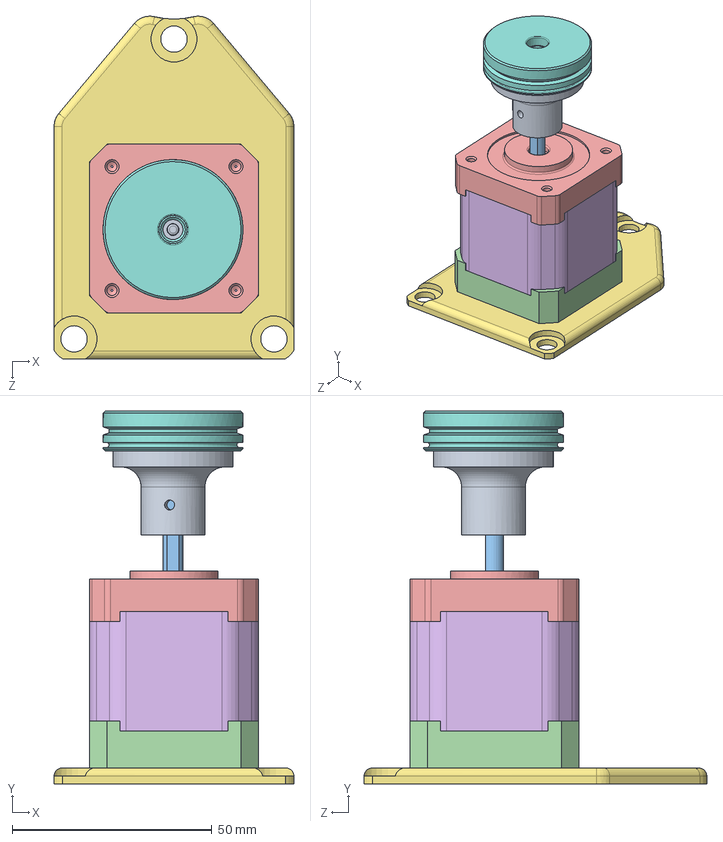
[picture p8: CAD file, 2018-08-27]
cad/twister3_bobbin-spinner.SLDASM
60.0 x 93.3 x 85.7 mm
twister3_spring_rotor_base
B222G-N52_kj-magnets x 2
NEMA 17 Stepper Motor Shaft
NEMA 17 Stepper Motor Bottom
NEMA 17 Stepper Motor Top
NEMA 17 Stepper Motor Middle
twister3_motor-mount
twister3_bobin

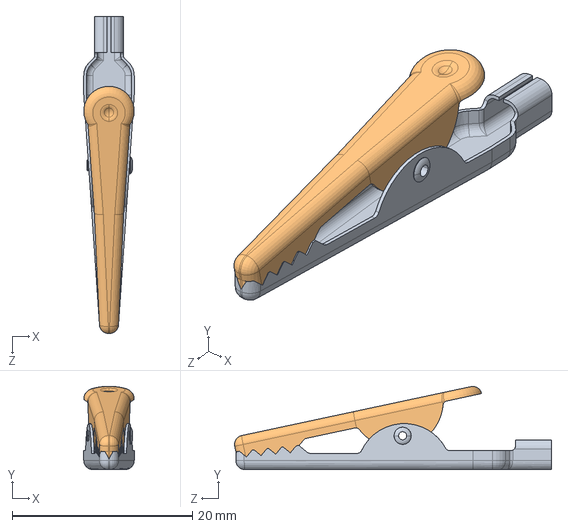
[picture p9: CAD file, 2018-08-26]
cad/crocodile-clip.SLDASM
5.60 x 9.22 x 35.1 mm
Crocodile clip_01.STEP
Crocodile clip_02.STEP

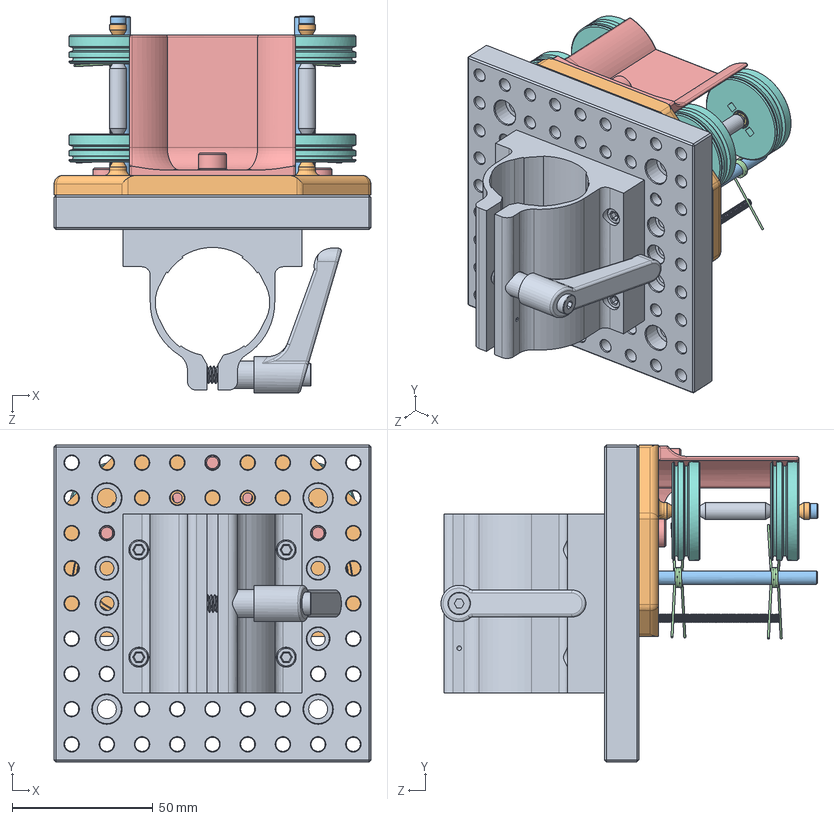
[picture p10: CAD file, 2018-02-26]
cad/twister3_feeder.SLDASM
112.5 x 112.5 x 133.8 mm
twister3_arm-base
98380A520_TYPE 416 STAINLESS STEEL DOWEL PIN x 2
90695A033_CLASS 04 STEEL THIN HEX NUT - DIN 439B x 4
91292A134_TYPE 18-8 SS SOCKET HEAD CAP SCREW x 3
94595A235_LOW-STRENGTH ZINC-PLATED STEEL THREADED ROD x 2
SMR73C_YZZ_AF2-bearings x 8
twister3_bobin x 4
twister3_bobbin-spacer x 2
twister3_bobbin-washer x 2
92290A131_TYPE 316 SS SOCKET HEAD CAP SCREW x 2
9271K210_MUSIC WIRE TORSION SPRING x 4
twister3_bobbin-shield

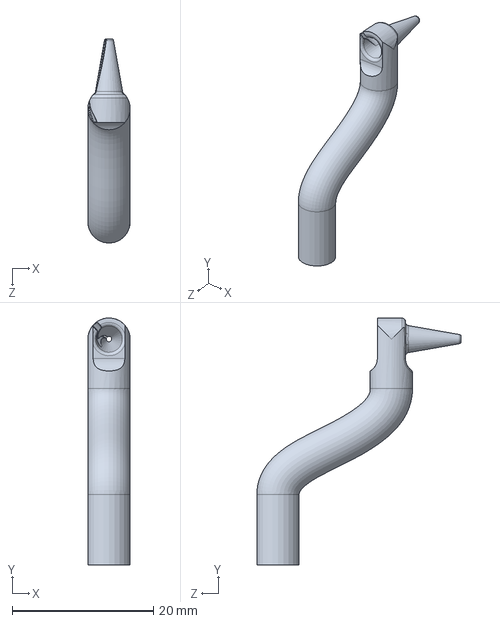
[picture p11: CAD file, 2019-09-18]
cad/twister3_wire-guide-base.SLDPRT
6.00 x 35.0 x 28.9 mm

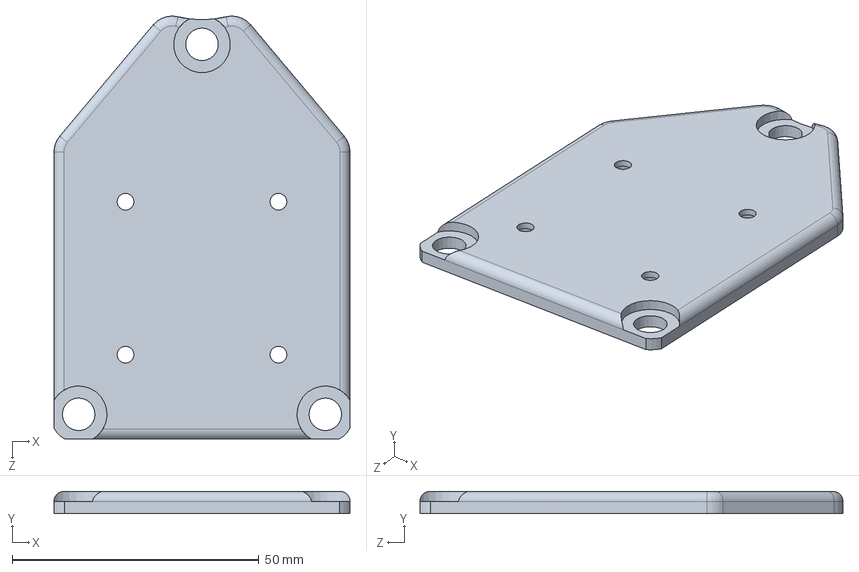
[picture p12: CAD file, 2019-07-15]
cad/twister3_motor-mount.sldprt
60.0 x 4.50 x 85.7 mm

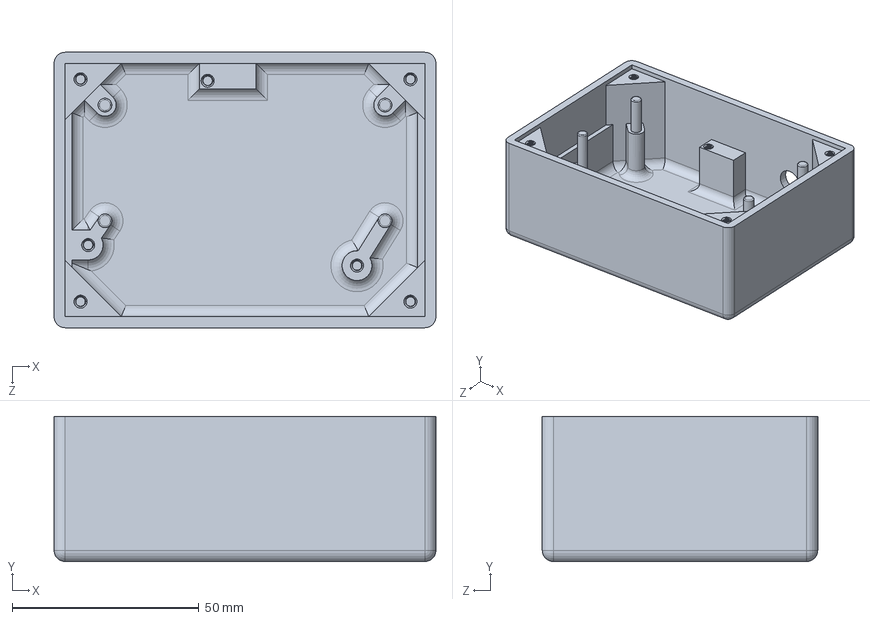
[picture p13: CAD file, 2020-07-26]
control-board/box/controller-box.SLDPRT
102.3 x 38.9 x 73.8 mm

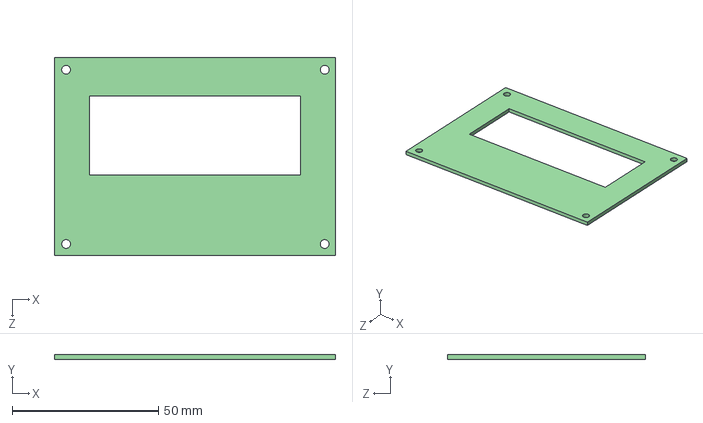
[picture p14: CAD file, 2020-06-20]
control-board/box/top-pcb.STEP
96.0 x 1.60 x 67.5 mm

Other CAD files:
cad/twister3_spring_rotor_mount.SLDPRT
control-board/box/bottom-pcb.STEP
cad/twister3_spring_rotor_base.SLDPRT
cad/twister3_twist-aligner_independent.sldprt
cad/90695A033_CLASS 04 STEEL THIN HEX NUT - DIN 439B.SLDPRT
cad/91292A024_TYPE 18-8 SS SOCKET HEAD CAP SCREW.SLDPRT
cad/91292A134_TYPE 18-8 SS SOCKET HEAD CAP SCREW.SLDPRT
cad/91390A100_ALLOY STEEL CUP POINT SET SCREW.SLDPRT
cad/92005A136_METRIC PAN HEAD PHILLIPS MACHINE SCREW.SLDPRT
cad/92290A131_TYPE 316 SS SOCKET HEAD CAP SCREW.SLDPRT
cad/9271K210_MUSIC WIRE TORSION SPRING.SLDPRT
cad/93245A098_NONMARRING FLAT POINT SOCKET SET SCREW.SLDPRT
cad/93600A267_METRIC TYPE 316 STAINLESS STEEL DOWEL PIN.SLDPRT
cad/94595A235_LOW-STRENGTH ZINC-PLATED STEEL THREADED ROD.SLDPRT
cad/94868A162_18-8 SS FEM THRDED HEX STANDOFF.SLDPRT
cad/98380A520_TYPE 416 STAINLESS STEEL DOWEL PIN.SLDPRT
cad/B222G-N52_kj-magnets.SLDPRT
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

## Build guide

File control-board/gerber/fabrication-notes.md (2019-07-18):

### Fabrication notes

 - Place UL mark and date code on backside of board.
 - Black solder mask on both sides of board. All vias to be tented.
 - High DPI White silk
 - Pad finish is ENIG.
 - Finished board thickness is 1.6 mm.

Files within this folder are defined as follows:

 - \*.GKO = board outline
 - \*.GTS = top solder mask
 - \*.GBS = bottom solder mask
 - \*.GTO = top silk screen
 - \*.GBO = bottom silk screen
 - \*.GTL = top copper
 - \*.G2L = layer 2 copper
 - \*.G2L = layer 3 copper
 - \*.GBL = bottom copper
 - \*.XLN = drill hits and sizes.
 - \*.gvp = [gerbv](http://gerbv.geda-project.org/) project file.

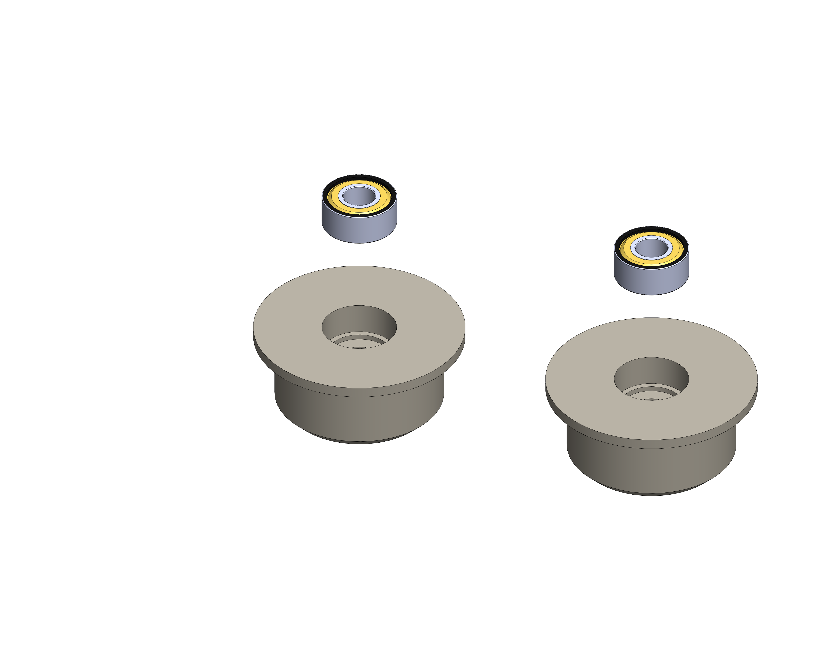
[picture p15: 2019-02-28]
paper/fig/stock-spool-assembly/step1.PNG

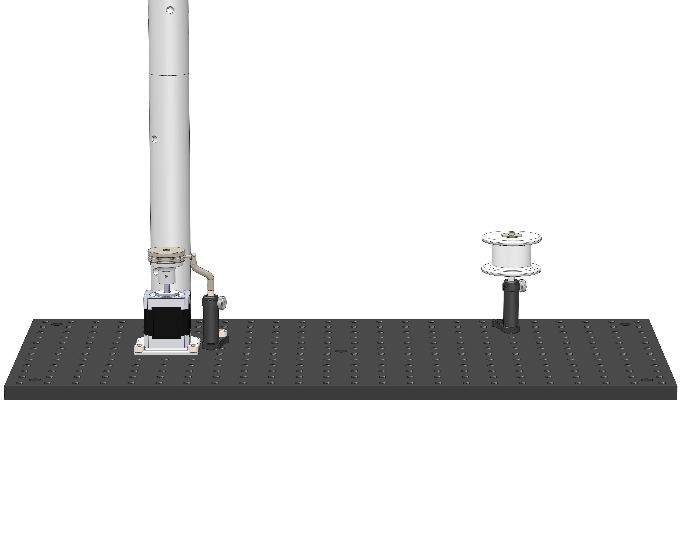
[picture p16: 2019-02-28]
paper/fig/usage/bob2.PNG

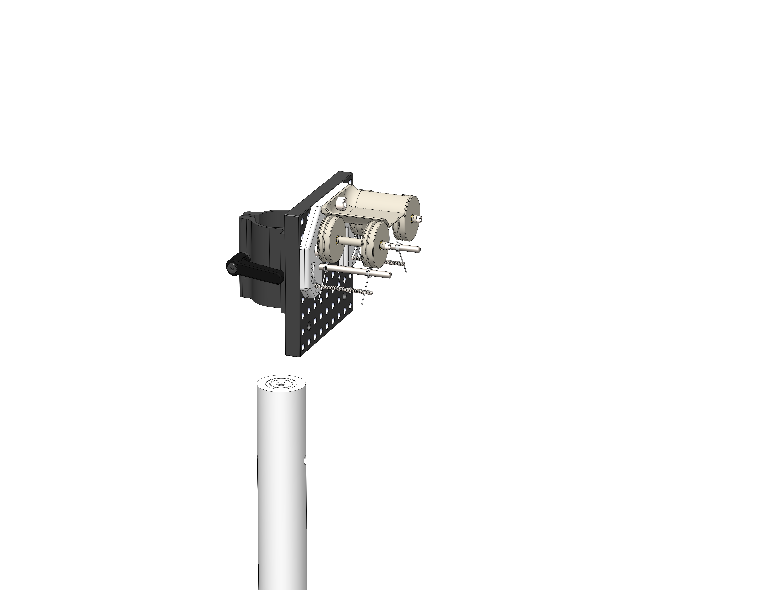
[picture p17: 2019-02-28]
paper/fig/twister3-assembly/step2.PNG

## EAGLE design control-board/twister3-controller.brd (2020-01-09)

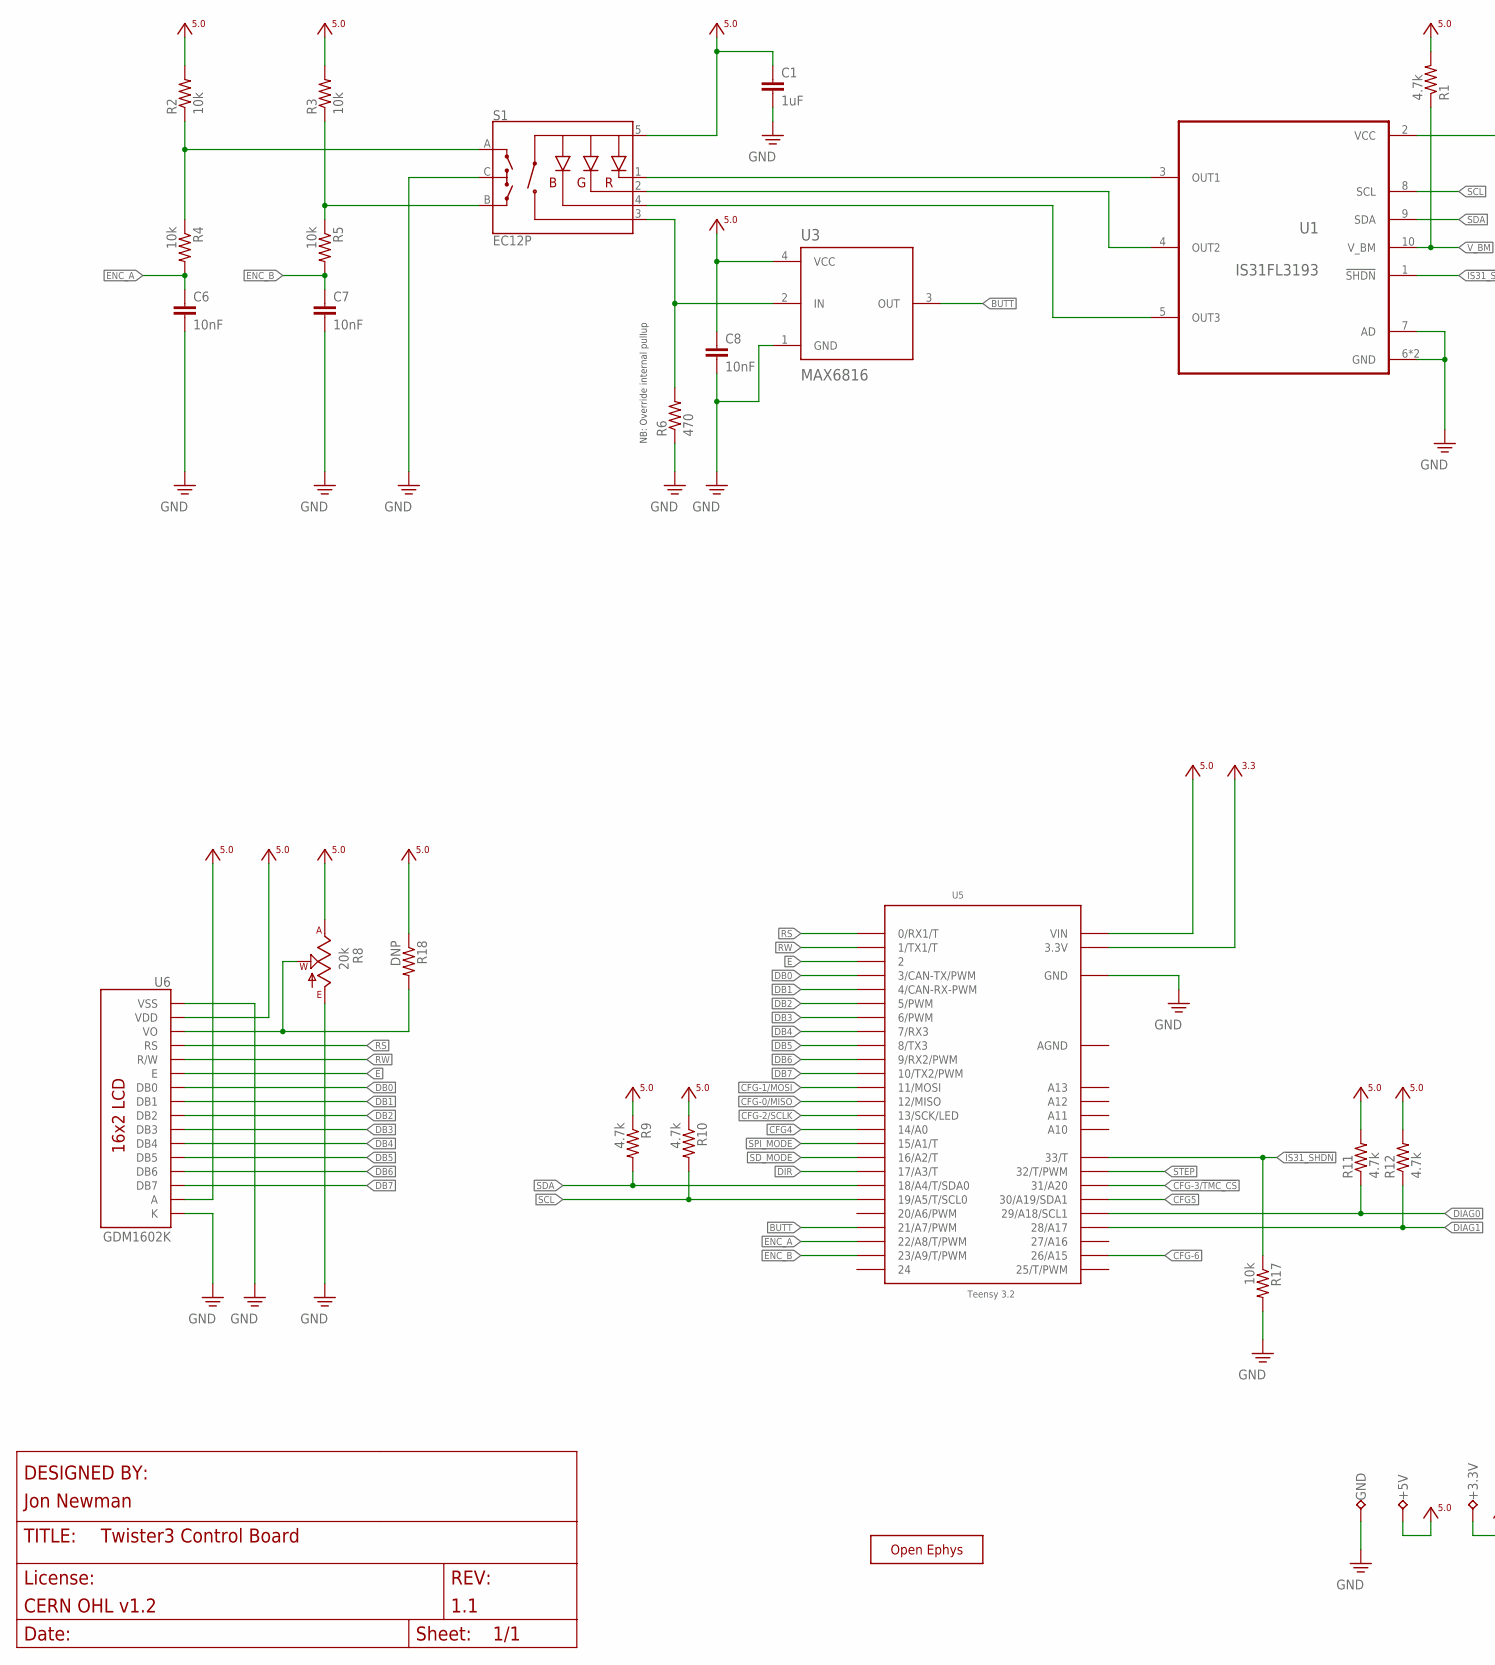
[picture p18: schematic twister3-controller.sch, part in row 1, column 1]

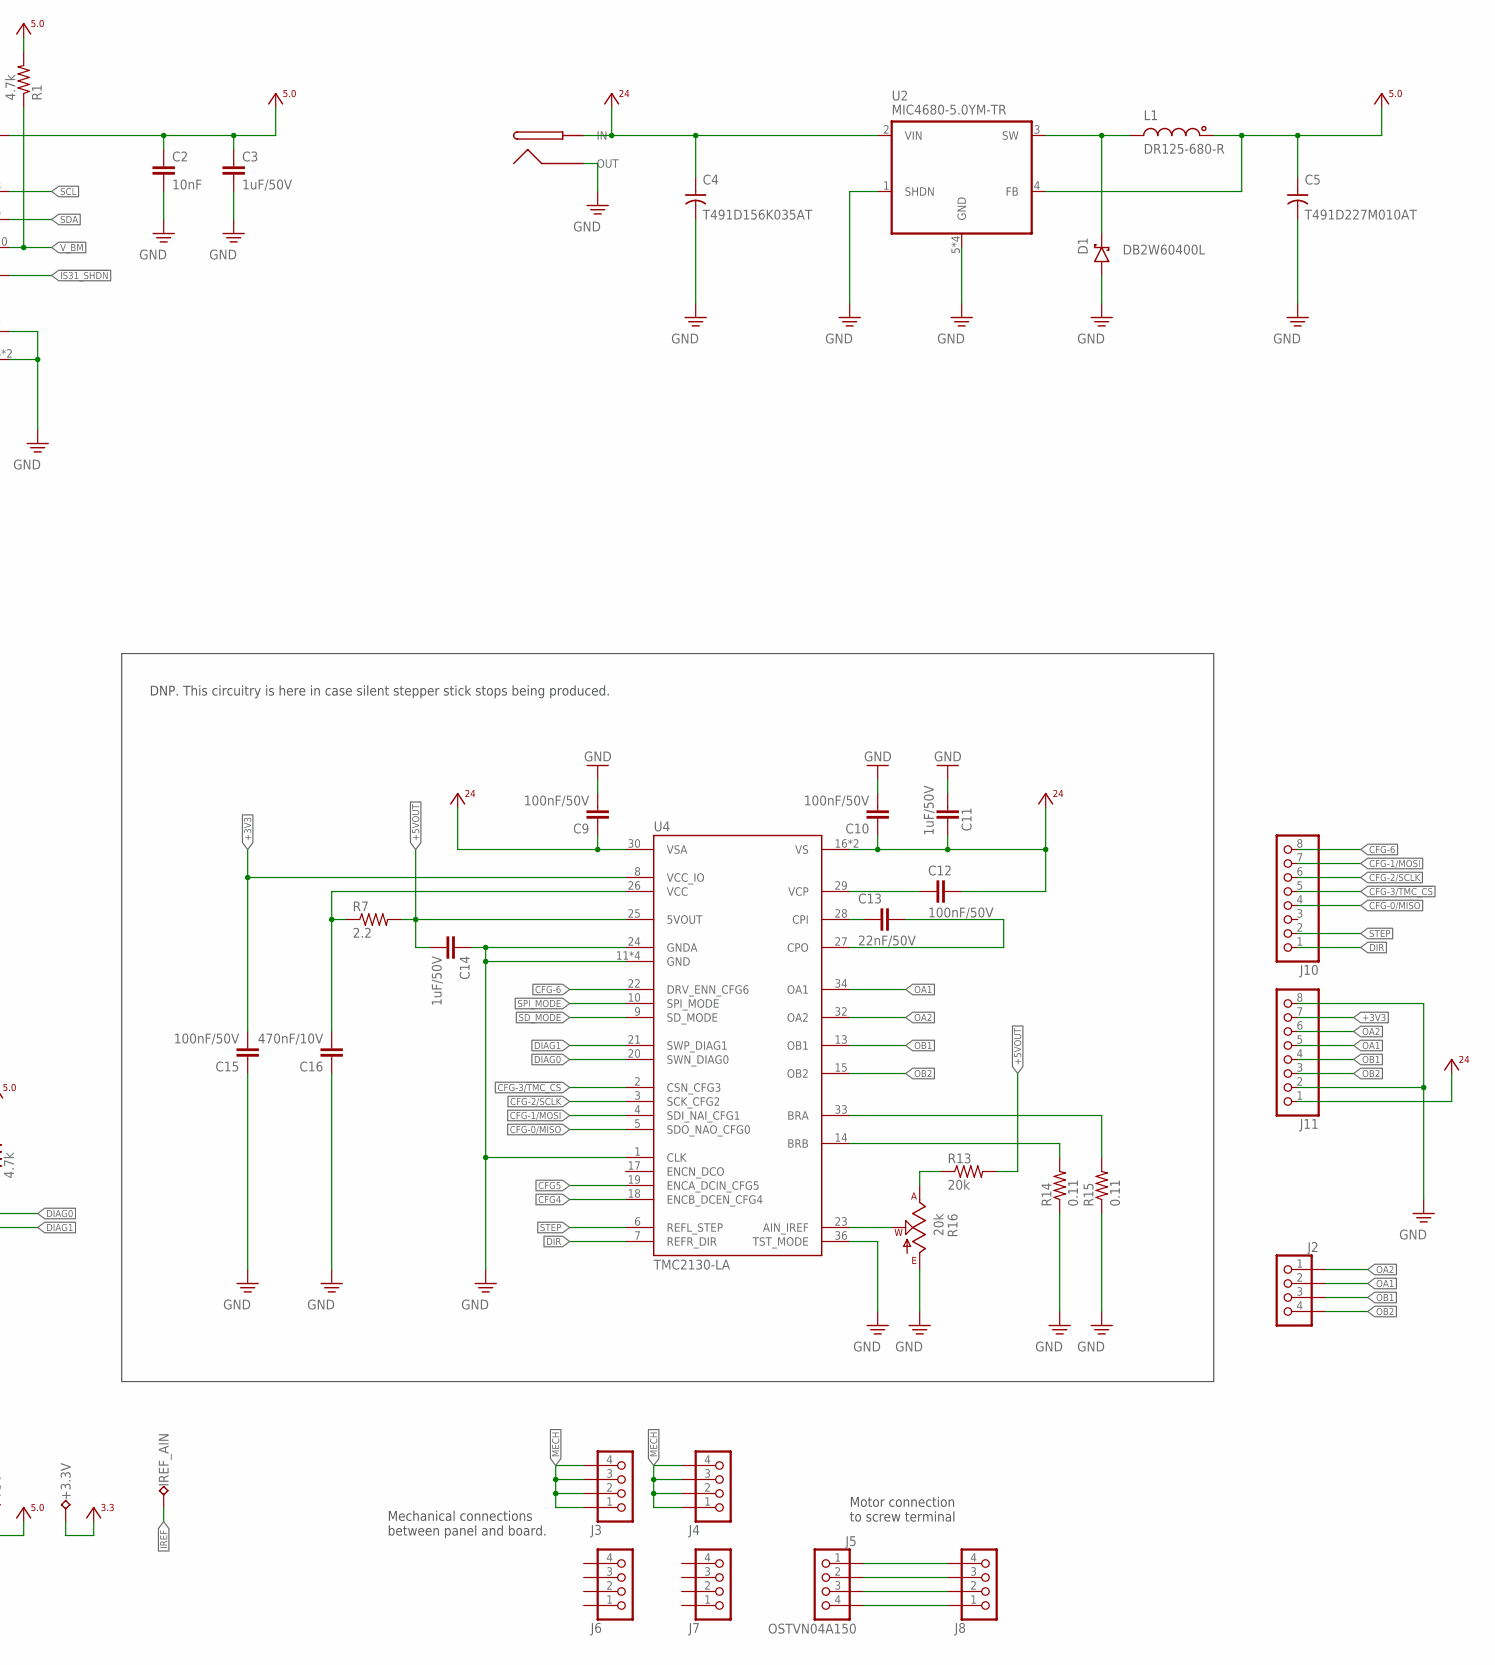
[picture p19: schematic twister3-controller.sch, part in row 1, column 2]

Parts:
+3.3V, +5V: TP_2MM; TESTPOINT_2MM
C1: 1uF; 0603
C2, C6, C7, C8: 10nF; 0603
C3, C11, C14: 1uF/50V; 0603
C4: T491D156K035AT; 7343M
C5: T491D227M010AT; 7343M
C9, C10, C12, C15: 100nF/50V; 0603
C13: 22nF/50V; 0402
C16: 470nF/10V; 0402
D1: DB2W60400L; SOD123
GND: TP_2MM; TESTPOINT_2MM
IREF_AIN: TP_2MM; TESTPOINT_2MM
J1: BARREL-JACK_PJ-063BH; PJ-063BH
J2, J6, J7: PINHD-1X4; 1X04
J3, J4, J8: PINHD-1X4_SMD-0.1"; JP4_SMD
J5: OSTVN04A150; 1X04
J10, J11: PINHD-1X08_2.54-S; 1X08-S
L1: DR125-680-R; DR125
R1, R9, R10, R11, R12: 4.7k; 0603
R2, R3, R4, R5, R17: 10k; 0603
R6: 470; 0603
R7: 2.2; 0402
R8, R16: 20k; SM-42/43X
R13: 20k; 0603
R14, R15: 0.11; 0805
R18: DNP; 0603
S1: EC12P; ENCODER_LED_3
U1: IS31FL3193; PWSON-N10-3X3
U2: MIC4680-5.0YM-TR; SOIC127P500X400-8N
U3: MAX6816; SOT143-4
U4: TMC2130-LA; QFN36-PAD
U5: Teensy 3.2; TEENSY_3.1_CYCLOPS
U6: GDM1602K; LCD-16X2
X1: OE-LOGO_14X10; OE-LOGO-14X10

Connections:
!IS31_SHDN: R17.1, U1.1 (!SHDN), U5.33 (33/T)
+3V3: +3.3V.1, C15.2, J11.7, U4.8 (VCC_IO), U5.3.3V, U5.3.3V2 (3.3V)
+5V0: +5V.1, C1.1, C2.1, C3.1, C5.+, C8.1, L1.1, R1.2, R2.2, R3.2, R8.1 (A), R9.1, R10.1, R11.2, R12.2, R18.1, S1.5 (+), U1.2 (VCC), U2.4 (FB), U3.4 (VCC), U5.VIN, U6.2 (VDD), U6.15 (A)
+5VOUT: C14.2, R7.2, R13.2, U4.25 (5VOUT)
+24V0: C4.+, C9.1, C10.1, C11.1, C12.1, J1.1 (IN), J11.1, U2.2 (VIN), U4.16 (VS), U4.30 (VSA), U4.31 (VS)
AGND: U5.AGND
BRA1: R15.2, U4.33 (BRA)
BRB1: R14.2, U4.14 (BRB)
BUTT: U3.3 (OUT), U5.21/A7 (21/A7/PWM)
CFG4: U4.18 (ENCB_DCEN_CFG4), U5.14/A0
CFG5: U4.19 (ENCA_DCIN_CFG5), U5.30 (30/A19/SDA1)
CFG-0/MISO: J10.4, U4.5 (SDO_NAO_CFG0), U5.12 (12/MISO)
CFG-1/MOSI: J10.7, U4.4 (SDI_NAI_CFG1), U5.11 (11/MOSI)
CFG-2/SCLK: J10.6, U4.3 (SCK_CFG2), U5.13 (13/SCK/LED)
CFG-3/!TMC_CS: J10.5, U4.2 (CSN_CFG3), U5.31 (31/A20)
CFG-6: J10.8, U4.22 (DRV_ENN_CFG6), U5.26 (26/A15)
CPI1: C13.2, U4.28 (CPI)
CPO1: C13.1, U4.27 (CPO)
DB0: U5.3 (3/CAN-TX/PWM), U6.7 (DB0)
DB1: U5.4 (4/CAN-RX-PWM), U6.8 (DB1)
DB2: U5.5 (5/PWM), U6.9 (DB2)
DB3: U5.6 (6/PWM), U6.10 (DB3)
DB4: U5.7 (7/RX3), U6.11 (DB4)
DB5: U5.8 (8/TX3), U6.12 (DB5)
DB6: U5.9 (9/RX2/PWM), U6.13 (DB6)
DB7: U5.10 (10/TX2/PWM), U6.14 (DB7)
DIAG0: R11.1, U4.20 (SWN_DIAG0), U5.29 (29/A18/SCL1)
DIAG1: R12.1, U4.21 (SWP_DIAG1), U5.28 (28/A17)
DIR: J10.1, U4.7 (REFR_DIR), U5.17/A3 (17/A3/T)
E: U5.2, U6.6 (E)
ENC_A: C6.1, R4.2, U5.22/A8 (22/A8/T/PWM)
ENC_B: C7.1, R5.2, U5.23/A9 (23/A9/T/PWM)
GND: C1.2, C2.2, C3.2, C4.-, C5.-, C6.2, C7.2, C8.2, C9.2, C10.2, C11.2, C14.1, C15.1, C16.1, D1.A, GND.1, J1.2 (OUT), J11.2, J11.8, R6.1, R8.3 (E), R14.1, R15.1, R16.3 (E), R17.2, S1.C, U1.6 (GND), U1.7 (AD), U1.PAD (GND), U2.1 (SHDN), U2.5 (GND), U2.6 (GND), U2.7 (GND), U2.8 (GND), U3.1 (GND), U4.1 (CLK), U4.11 (GND), U4.12 (GND), U4.24 (GNDA), U4.35 (GND), U4.36 (TST_MODE), U4.TP (GND), U5.GND, U5.GND2 (GND), U6.1 (VSS), U6.16 (K)
IREF: IREF_AIN.1, R16.2 (W), U4.23 (AIN_IREF)
MECH: J3.1, J3.2, J3.3, J3.4, J4.1, J4.2, J4.3, J4.4
unnamed: R2.1, R4.1, S1.A
unnamed: R6.2, S1.3 (SW), U3.2 (IN)
unnamed: S1.1 (-R), U1.3 (OUT1)
unnamed: R3.1, R5.1, S1.B
unnamed: J5.1, J8.4
unnamed: J5.2, J8.3
unnamed: J5.3, J8.2
unnamed: J5.4, J8.1
unnamed: S1.2 (-G), U1.4 (OUT2)
unnamed: R8.2 (W), R18.2, U6.3 (VO)
OA1: J2.2, J11.5, U4.34 (OA1)
OA2: J2.1, J11.6, U4.32 (OA2)
OB1: J2.3, J11.4, U4.13 (OB1)
OB2: J2.4, J11.3, U4.15 (OB2)
RS: U5.0 (0/RX1/T), U6.4 (RS)
RW: U5.1 (1/TX1/T), U6.5 (R/W)
SCL: R10.2, U1.8 (SCL), U5.19/A5 (19/A5/T/SCL0)
SDA: R9.2, U1.9 (SDA), U5.18/A4 (18/A4/T/SDA0)
SD_MODE: U4.9 (SD_MODE), U5.16/A2 (16/A2/T)
SPI_MODE: U4.10 (SPI_MODE), U5.15/A1 (15/A1/T)
STEP: J10.2, U4.6 (REFL_STEP), U5.32 (32/T/PWM)
SUPPY4: S1.4 (-B), U1.5 (OUT3)
SW: D1.C, L1.2, U2.3 (SW)
VCC1: C16.2, R7.1, U4.26 (VCC)
VCP1: C12.2, U4.29 (VCP)
VREF2: R13.1, R16.1 (A)
V_BM: R1.1, U1.10 (V_BM)

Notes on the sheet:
NB: Override internal pullup
Mechanical connections between panel and board.
Motor connection to screw terminal
DNP. This circuitry is here in case silent stepper stick stops being produced.

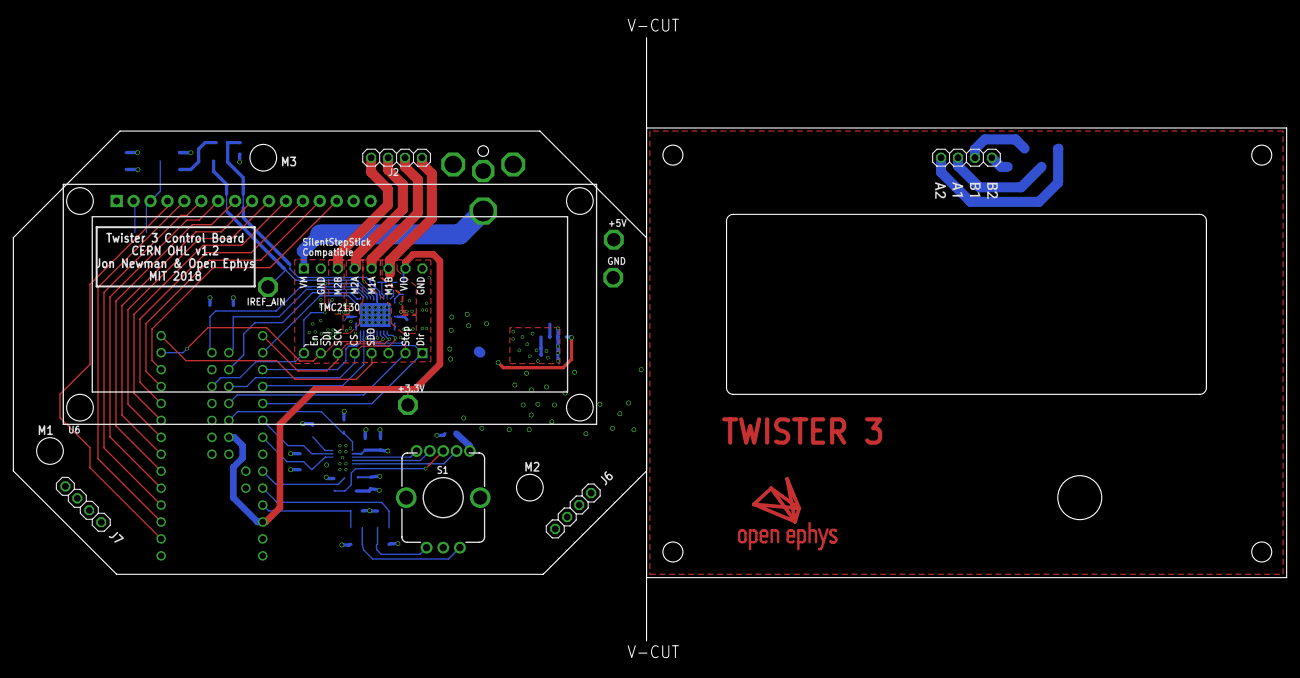
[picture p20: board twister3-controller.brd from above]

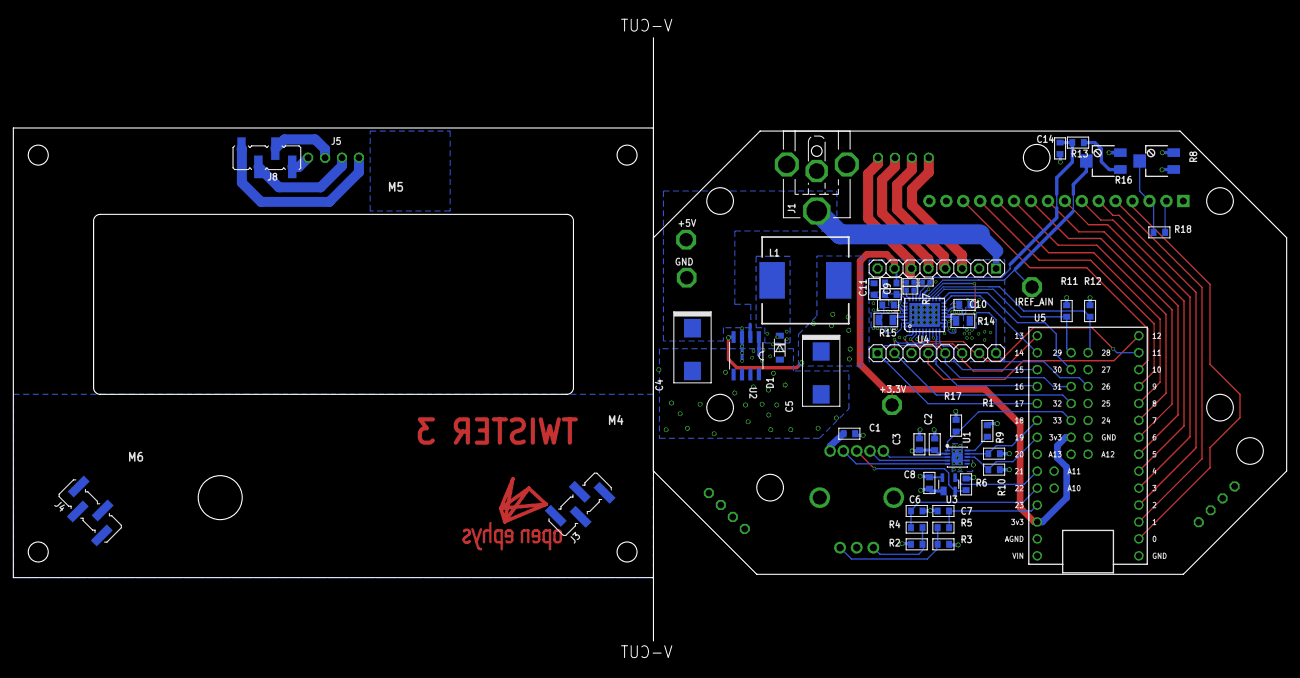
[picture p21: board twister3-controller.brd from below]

Board: 4 copper layers, 191.0 x 90.5 mm, 58 parts (47 on the bottom side), 61 nets.

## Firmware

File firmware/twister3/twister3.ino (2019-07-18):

// ----------------------------------------------------------------------------
// "THE BEER-WARE LICENSE" (Revision 42):
// JPN wrote this file. As long as you retain this notice you
// can do whatever you want with this stuff. If we meet some day, and you think
// this stuff is worth it, you can buy me a beer in return.
// ----------------------------------------------------------------------------

#include <EEPROM.h>
#include <LiquidCrystal.h>
#include <TeensyStep.h>
#include <Encoder.h>
#include <i2c_t3.h>

//#define DEBUG
//#include <Serial.h>

// Button read parameters
#define HOLD_MSEC 300

// Stepper parameters
#define DETENTS 200
#define USTEPS_PER_REV (DETENTS * 16)

// Stepper driver pins
#define MOT_DIR 17
#define MOT_STEP 32
#define MOT_CFG0_MISO 12
#define MOT_CFG1_MOSI 11
#define MOT_CFG2_SCLK 13
#define MOT_CFG3_TMCCS 31
#define MOT_CFG4 14
#define MOT_CFG5 30
#define MOT_CFG6_EN 26
#define MOT_SPI_MODE 15
#define MOT_SD_MODE 16
#define MOT_DIAG0 29
#define MOT_DIAG1 28

// I2C
#define SDA 18
#define SCL 19

// RGB Driver
#define IS31_ADDR 0x68
#define IS31_SHDN 33

// Rotary encoder pins
#define ENC_A 22
#define ENC_B 23
#define ENC_BUTT 21

// Settings address start byte.
#define SETTINGS_ADDR_START 0

// Rotary encoder state
long last_encoder_pos_ = 0;

// Device Mode
int mode_idx_ = 0;
const int num_modes_ = 2;
float mode_idx_inc_ = 10000.0;

// Device parameters (match number of modes)
// [0] for tt twisting
// [1] for spool winding
float forward_turns_[num_modes_] = {50, 100};
float back_turns_[num_modes_] = {0, 0};
float turn_speed_rpm_[num_modes_] = {700, 100};
const float knob_gain_[num_modes_] = {0.25, 1};

// Start trigger
volatile bool start_requested_ = false;

// Selected parameter state
enum SelectedParam { fwd_turns, bck_turns, turn_spd, sel_mode, num_params };
volatile SelectedParam selected_param_ = fwd_turns;

// Stepper motor
Stepper motor_(MOT_STEP, MOT_DIR);
StepControl controller_; // Use default settings

// Rotary encoder
Encoder encoder_(ENC_B, ENC_A);

// LCD
volatile bool disp_update_requested = false;
LiquidCrystal lcd(0, 1, 2, 3, 4, 5, 6, 7, 8, 9, 10);

elapsedMillis sinceButtonChange;

// Setting state load/save
void loadSettings()
{
    int addr = SETTINGS_ADDR_START;

    byte good_settings = 0x0;
    EEPROM.get(addr, good_settings); // check good settings flag
    if (good_settings != 0x12) return;

    for (int i = 0; i < num_modes_; i++) {
        EEPROM.get(addr += sizeof(float), forward_turns_[i]);
        EEPROM.get(addr += sizeof(float), back_turns_[i]);
        EEPROM.get(addr += sizeof(float), turn_speed_rpm_[i]);
    }

    Serial.println("Fwd turns:");
    Serial.println(forward_turns_[0]);
}

void saveSettings()
{
    int addr = SETTINGS_ADDR_START;
    EEPROM.put(addr, 0x12); // good settings flag

    for (int i = 0; i < num_modes_; i++) {
        EEPROM.put(addr += sizeof(float), forward_turns_[i]);
        EEPROM.put(addr += sizeof(float), back_turns_[i]);
        EEPROM.put(addr += sizeof(float), turn_speed_rpm_[i]);
    }
}

// Return code
// -2 : Wrong value compared to desired_value
//  1 : Normal button press.
//  2 : Hold value maintained for longer than wait period.
// NOTE: Need interrupts enabled for this to work properly.
static int readButton(int pin,
                      int *value,
                      int desired_value = -1)
{
    // Log button change time
    sinceButtonChange = 0;

    // Make sure button state equals desired value
    *value = digitalReadFast(pin);
    if (desired_value != -1 && desired_value != *value)
        return -2;

    // See if the user keeps button held for HOLD_MSEC
    while (sinceButtonChange < HOLD_MSEC) {
        if (*value != digitalReadFast(pin))
            return 1;
    }

    return 2;
}

int executeTwist(void)
{
    int rc = 0;

    // Unsleep the driver
    digitalWriteFast(MOT_CFG6_EN, LOW);

    // Set speed
    auto max_speed = (float)USTEPS_PER_REV * turn_speed_rpm_[mode_idx_] / 60.0;
    motor_.setMaxSpeed(max_speed);
    motor_.setAcceleration(max_speed / 3);

    // Change RBG to red and tell user we are turning
    setRGBColor(0xFF, 0x00, 0x00);
    lcd.clear();
    lcd.print(F("Forward..."));

    // Forward motion
    motor_.setTargetRel((long)forward_turns_[mode_idx_] * (long)USTEPS_PER_REV);
    controller_.moveAsync(motor_);
    while (controller_.isRunning() && start_requested_) {
        delay(10);
    }

    lcd.clear();
    lcd.print(F("Backward..."));

    // Backward motion
    motor_.setTargetRel(-(long)back_turns_[mode_idx_] * (long)USTEPS_PER_REV);
    controller_.moveAsync(motor_);
    while (controller_.isRunning() && start_requested_) {
        delay(10);
    }

    if (!start_requested_) {
        controller_.emergencyStop();
        lcd.clear();
        lcd.print(F("Turn aborted."));
        rc = 1;
    } else {
        lcd.clear();
        lcd.print(F("Turn complete."));
    }

    // Sleep the driver
    digitalWriteFast(MOT_CFG6_EN, HIGH);

    // Reset RGB based on mode
    modeToRGB();

    // 0 = successful move
    // 1 = emergency stop
    return rc;
}

// Return difference in encoder position since last read
int getEncoderDiff()
{
    long curr = encoder_.read();
    int diff = curr - last_encoder_pos_;
    last_encoder_pos_ = curr;
    if (diff)
        disp_update_requested = true;
    return diff;
}

void setRGBColor(byte r, byte g, byte b)
{
    // Set PWM state
    Wire.beginTransmission(IS31_ADDR);
    Wire.write(0x04);
    Wire.write(r);
    Wire.write(g);
    Wire.write(b);
    Wire.endTransmission();

    // Update PWM
    Wire.beginTransmission(IS31_ADDR);
    Wire.write(0x07);
    Wire.write(0x00);
    Wire.endTransmission();

}

void modeToRGB() {

    switch (mode_idx_) {
    case 0:
        setRGBColor(0x33, 0x55, 0xFF);
        break;
    case 1:
        setRGBColor(0x00, 0xFF, 0x55);
        break;
    }
}

void setupRGB()
{
    // I2C for RGB LED
    Wire.begin(I2C_MASTER, 0x00, I2C_PINS_18_19, I2C_PULLUP_EXT, 400000);
    Wire.setDefaultTimeout(200000); // 200ms

    // Enable LED current driver
    pinMode(IS31_SHDN, OUTPUT);
    digitalWriteFast(IS31_SHDN, HIGH);
    delay(1);

    // Set max LED current
    Wire.beginTransmission(IS31_ADDR);
    Wire.write(0x03);
    Wire.write(0x08); // Set max current to 5 mA
    Wire.endTransmission();

    // Default color
    modeToRGB();

    // Enable current driver
    Wire.beginTransmission(IS31_ADDR);
    Wire.write(0x00);
    Wire.write(0x20); // Enable current driver
    Wire.endTransmission();
}

void configMotor()
{
    // TODO: use spi interface and get to work in silent mode
    pinMode(MOT_SPI_MODE, OUTPUT);
    pinMode(MOT_SPI_MODE, LOW);

    // Chopper off time
    pinMode(MOT_CFG0_MISO, OUTPUT);
    digitalWriteFast(MOT_CFG0_MISO, LOW);

    // 16-step spreadcycle: GFG2 = open, CFG 1 = gnd
    // TODO: the led is preventing cfg2 from being open, I think. Instead, I'm
    // using 16-ustep without interp...
    //pinMode(MOT_CFG1_MOSI, INPUT);
    pinMode(MOT_CFG1_MOSI, OUTPUT);
    //digitalWriteFast(MOT_CFG1_MOSI, LOW);
    digitalWriteFast(MOT_CFG1_MOSI, HIGH);
    //pinMode(MOT_CFG2_SCLK, INPUT);
    pinMode(MOT_CFG2_SCLK, OUTPUT);
    digitalWriteFast(MOT_CFG2_SCLK, HIGH);

    // Use external sense resistors
    pinMode(MOT_CFG3_TMCCS, INPUT);

    // Chopper hysteresis
    pinMode(MOT_CFG4, OUTPUT);
    digitalWriteFast(MOT_CFG4, LOW);

    // Chopper blank time
    pinMode(MOT_CFG5, OUTPUT);
    digitalWriteFast(MOT_CFG5, HIGH);

    // Disable motor
    pinMode(MOT_CFG6_EN, OUTPUT);
    digitalWriteFast(MOT_CFG6_EN, HIGH);
}

void toggleParam()
{
    int val;
    auto hold = readButton(ENC_BUTT, &val, HIGH);

    noInterrupts();
    switch (hold) {
        case 2: {
            start_requested_ = true;
            break;
        }
        case 1: {
            if (start_requested_) {
                start_requested_ = false;
                setRGBColor(0x00, 0xFF, 0x55);
            } else {
                int sm = (int)selected_param_;
                sm++;
                if (sm >= num_params)
                    sm = 0;
                selected_param_ = (SelectedParam)sm;
            }
            break;
        }
    }

    disp_update_requested = true;

    interrupts();
    return;
}

void setup()
{
    Serial.begin(9600);

    pinMode(ENC_BUTT, INPUT);
    attachInterrupt(ENC_BUTT, toggleParam, RISING);

    // Configure and Disable motor
    configMotor();

    setupRGB();

    lcd.begin(16, 2);
    lcd.print(F("twister3"));
    lcd.setCursor(0, 1);
    lcd.print(F("JPN MWL MIT"));

    delay(2000);
    disp_update_requested = true;

    // Get parameters from last use
    loadSettings();
}

void loop()
{
    int diff = getEncoderDiff();

    if (diff) {

        switch (selected_param_) {

            case fwd_turns: {
                forward_turns_[mode_idx_]
                    += (float)diff * knob_gain_[mode_idx_];
                if (forward_turns_[mode_idx_] < 0)
                    forward_turns_[mode_idx_] = 0;
                break;
            }
            case bck_turns: {
                back_turns_[mode_idx_]
                    += (float)diff * knob_gain_[mode_idx_];
                if (back_turns_[mode_idx_] < 0)
                    back_turns_[mode_idx_] = 0;
                break;
            }
            case turn_spd: {
                turn_speed_rpm_[mode_idx_]
                    += (float)diff * knob_gain_[mode_idx_];
                if (turn_speed_rpm_[mode_idx_] < 0)
                    turn_speed_rpm_[mode_idx_] = 0;
                break;
            }
            case sel_mode: {

                mode_idx_inc_ += (float)diff * 0.25; // HACK :)
                mode_idx_ = (int)mode_idx_inc_ % num_modes_;
                modeToRGB();
                break;
            }
        }
    }

    if (disp_update_requested) {

        lcd.clear();

        // Mode in upper right
        lcd.setCursor(15, 0);
        switch (mode_idx_) {
            case 0:
                lcd.print(F("0"));
                break;
            case 1:
                lcd.print(F("1"));
                break;
        }

        // State info
        lcd.setCursor(0, 0);
        switch (selected_param_) {

            case fwd_turns: {
                lcd.print(F("Fwd. turns:"));
                lcd.setCursor(0, 1);
                lcd.print((int)forward_turns_[mode_idx_]);
                break;
            }
            case bck_turns: {
                lcd.print(F("Back turns:"));
                lcd.setCursor(0, 1);
                lcd.print((int)back_turns_[mode_idx_]);
                break;
            }
            case turn_spd: {
                lcd.print(F("Speed (RPM):"));
                lcd.setCursor(0, 1);
                lcd.print((int)turn_speed_rpm_[mode_idx_]);
                break;
            }
            case sel_mode: {
                lcd.print(F("Mode:"));
                lcd.setCursor(0, 1);
                switch (mode_idx_) {
                    case 0:
                        lcd.print(F("Twist TT (0)"));
                        break;
                    case 1:
                        lcd.print(F("Load bobbin (1)"));
                        break;
                }
                break;
            }
        }

        disp_update_requested = false;
    }

    if (start_requested_) {
        saveSettings(); // EEPROM good for ~100,000 twists
        executeTwist();
        start_requested_ = false;
    }
}

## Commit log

2017-11-23 Initial commit.
    [93805A632_18-8 STAINLESS STEEL THREADED ROD.SLDPRT, 9657K267_STEEL COMPRESSION SPRING.SLDPRT, 9657K810_STEEL COMPRESSION SPRING.SLDPRT, C1545_M-Solidworks.sldp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]
2017-11-29 TT spool portion of twister
    - 4 pre-loaded TT bobins on adjustable post
    [9271K210_MUSIC WIRE TORSION SPRING.SLDPRT, 92855A317_TYPE 18-8 SS LOW PROFILE SOCKET CAP SCREW.SLDPRT, 92871A175_SS UNTHRD SPACER.SLDPRT, 93805A632_18-8 STAINL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]
2017-11-30 Finished basic mechanical components
    - Added motor mounts, spinning mechanism, and spool loading adapters
    - Twister3.sldasm has the complete assembly
    [91292A024_TYPE 18-8 SS SOCKET HEAD CAP SCREW.SLDPRT, 9271K210_MUSIC WIRE TORSION SPRING.SLDPRT, 92855A317_TYPE 18-8 SS LOW PROFILE SOCKET CAP SCREW.SLDPRT, 928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]
2017-12-01 Addressed Jakob's comments
    - The comments are shown here
    - All are addressed but I opted to keep the screws holding the bearings
    instead of using dowels
    you got a few missing components there that are not in the right path
    the loading stepper motor holder looks odd instead of compressing with
    set screws i would screw the motor into a adapter plate from below or
    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
    [91292A024_TYPE 18-8 SS SOCKET HEAD CAP SCREW.SLDPRT, 9271K210_MUSIC WIRE TORSION SPRING.SLDPRT, 92855A317_TYPE 18-8 SS LOW PROFILE SOCKET CAP SCREW.SLDPRT, 928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]
2017-12-02 Final touches before first fabrication iteration
    - 3D parts off to printers
    - Ordering TL and MMC parts
    [NEMA 17 Stepper Motor Assembly_1.sldasm, NEMA 17 Stepper Motor Bottom_1.sldprt, NEMA 17 Stepper Motor Middle_1.sldprt, NEMA 17 Stepper Motor Shaft_1.sldprt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]
2018-01-02 Updates to deal with unstable spinning in rev 1.0
    - Larger moment of inertia in hanger
    - Other minor fixes
    [91292A024_TYPE 18-8 SS SOCKET HEAD CAP SCREW.SLDPRT, 9271K210_MUSIC WIRE TORSION SPRING.SLDPRT, 9271K578_MUSIC WIRE TORSION SPRING.SLDPRT, 92855A317_TYPE 18-8 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]
2018-01-04 Added 3d printed spring-loaded spinning base
    we'll likely want to try a few different thicknesses/spring constants
    [twister3_spring-top.sldprt, twister3_spring_rotor_base.SLDPRT]
2018-01-05 added 2nd spring clip holder variant
    [twister3_spring-top.sldprt, twister3_spring-top_b.sldprt]
2018-02-26 Revisions after using prototype pretty extensively
    - Major design simplification
    - All attachment at motor is done by alignment pin + magnets
    - Bobbins are larger and have flat channels for TT wire
    - Bobbins are held to spinner via magnets for loading
    - The hanging spinners have been removed because they dont work
    - The non-functional leaf-spring spinners have been removed
    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
    [90695A033_CLASS 04 STEEL THIN HEX NUT - DIN 439B.SLDPRT, 91292A024_TYPE 18-8 SS SOCKET HEAD CAP SCREW.SLDPRT, 91292A134_TYPE 18-8 SS SOCKET HEAD CAP SCREW.SLDP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]
2018-02-26 Added README and reorganized repo
    - Now that the thing is working, should clean up a bit.
    [90695A033_CLASS 04 STEEL THIN HEX NUT - DIN 439B.SLDPRT, 91292A024_TYPE 18-8 SS SOCKET HEAD CAP SCREW.SLDPRT, 91292A134_TYPE 18-8 SS SOCKET HEAD CAP SCREW.SLDP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]
2018-03-01 Added primitive firmware for controller.
    [twister3_stock-spool-bearing-case.STL]
2018-04-17 Started twister3 control board
    - Schematic is not finished
    - Basically a mashup of teensy, rotary encoder knob, debounce IC, silent
    stepper stick.
    - Idea is to keep silent stepper stick form factor so that you can
    either plug one in or populate the board when the become obsolete
    [twister3-controller.brd, twister3-controller.sch]
2018-07-04 Pretty much done with r1.0 of control board
    - Stacking PCB design
    - Top PCB is a panel that fits into a plastic enclosure
    - Bottom holds electronics (Teensy 3.2, LCD, motor driver, encoder, etc)
    - 0.1" headers hold the two boards together
    - I'm trying to use hacked GND press clips to clip the LCD PCB to the
    panel board instead of screws/standoffs. The goal is the two PCBs should
    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
    [twister3-controller.GBL, twister3-controller.GBO, twister3-controller.GBS, twister3-controller.GKO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]
2018-07-09 Updates to cad and README
    - Improved bobbin base. Use a hex standoff instead of tapping M3s right
    into plastic
    - Improved wire guide.
    - Other small CAD changes
    - Added to README. e.g. put links to BOM
    [94868A162_18-8 SS FEM THRDED HEX STANDOFF.SLDPRT, twister3_arm-base.SLDPRT, twister3_arm-base.STL, twister3_spinner.SLDASM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]
2018-07-11 Complete rev 1.0 of control board
    - Off to fab
    [twister3-controller.GBL, twister3-controller.GBO, twister3-controller.GBS, twister3-controller.GKO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]
2018-07-24 Made arm-base hex insert slightly bigger
    - Press fit was a bit intense
    - STL updated and uploaded to shapeways
    [twister3_arm-base.SLDPRT, twister3_arm-base.STL]
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2018-08-09 Updated control board after assembly
    - Removed redudant mechanical connectors
    - Added positions for SMD nuts on bottom of panel board
    - Replace most 0805 components with 0603
    - Other minor changes
    [twister3-controller.GBL, twister3-controller.GBO, twister3-controller.GBS, twister3-controller.GKO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]
2018-08-11 Small updates to control board
    - Tighter tolerance on LCD cutout
    - Added test points
    [twister3-controller.GBL, twister3-controller.GBO, twister3-controller.GBS, twister3-controller.GKO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]
2018-08-26 CAD up to date for creation of manual
    - Added different display states etc that will result in figures for the
    manual
    [90695A033_CLASS 04 STEEL THIN HEX NUT - DIN 439B.SLDPRT, 91292A024_TYPE 18-8 SS SOCKET HEAD CAP SCREW.SLDPRT, 91292A134_TYPE 18-8 SS SOCKET HEAD CAP SCREW.SLDP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]
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2018-08-27 Convert binary files to git LFS
    - Some updates to resources
    - Added control box usage figure
    [twister3_bobbin-spinner.SLDASM, twister3_trode-spinner.SLDASM]
2018-09-04 Updates to control board after assembly of rev 1.1
    - Better retaining mechanism for top panel
    - Simplified and updated BOM on the google doc to match this version
    [twister3-controller.GBL, twister3-controller.GBO, twister3-controller.GBS, twister3-controller.GTL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]
2019-01-21 Some work on MANUAL.txt
    - Added missing MANUAL.pdf
    - Updated some contruction steps
    [twister3-controller.sch]
2019-02-20 Minor clarifying updates to MANUAL and schematic
    [twister3-controller.sch]
2019-02-21 Modified wire guide s.t. it gets closer to bobbin
    - Wire guide can now extend over motor mount so that wire can be cleanly
    feed onto the bobbin during loading
    [twister3_motor-mount.sldprt, twister3_spring-top.sldprt, twister3_spring_rotor_base.SLDPRT, twister3_trode-spinner.SLDASM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]
2019-02-22 Added overview of mechanics to figure 1.
    [twister3_motor-mount.sldprt, twister3_trode-spinner.SLDASM]
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2019-02-23 Removed trimpot access in control board front panel
    - Trimpots should be set during assembly and glued, access is not
    required during operaiton. Also, current trimpot only works if the
    silent stepper stick module is not used with is not the default case.
    - Also, removed reset switch (since this can be done by removing
    power...)
    [twister3-controller.GBL, twister3-controller.GBS, twister3-controller.GKO, twister3-controller.GTL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]
2019-02-23 Some minor updates to MANUAL.*
    - Also updated control board schematic to indicate that stepper driver
    circuit should not be populated if you are using a silent stepper stick.
    - At this point, I'm considering the MANUAL deprecated and moving its
    contents to the paper, which will act as a manual when it is finished.
    [twister3-controller.sch]
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2019-02-27 Update cad with views and simulations for paper
    - Simulation of leaf spring deformation
    - Assemblies have lots of alternative views for figures in paper
    [91390A100_ALLOY STEEL CUP POINT SET SCREW.SLDPRT, B222G-N52_kj-magnets.SLDPRT, MSL2-Solidworks.sldprt, twister3_bobin.SLDASM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]
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2019-04-30 Fixes to figures to include wire aligner
    - The usage figure still needs to be updated
    [twister3_motor-mount.sldprt, twister3_trode-spinner.SLDASM, twister3_twist-aligner.sldprt]
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2019-07-15 Address Ming's comments in the figures
    - Added thumwheel
    - Fixed issues in labelling inconsistencies
    - Added mouse and rat tt data to tt-mech figure
    [twister3_bobin.SLDASM, twister3_motor-mount.sldprt, twister3_screw_thumbwheel.SLDPRT]
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2020-06-20 Fixed asymmetric pcb placement in control-box encolsure
    - Hole placement was a bit off center resulting in asymmetic tolerances
    on the sides of the enclosure
    - Supressed snap in tabs per Filipe's request
    [bottom-pcb.SLDPRT, bottom-pcb.STEP, controller-box-assem.SLDASM, controller-box.SLDPRT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]
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2020-07-26 Fixed shifted power input hole on the 3D printed controller case
    - It was improperly offset from the side
    [controller-box-assem.SLDASM, controller-box.SLDPRT]

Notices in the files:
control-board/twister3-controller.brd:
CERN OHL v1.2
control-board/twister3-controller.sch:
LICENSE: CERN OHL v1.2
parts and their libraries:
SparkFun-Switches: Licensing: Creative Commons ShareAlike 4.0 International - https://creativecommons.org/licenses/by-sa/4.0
